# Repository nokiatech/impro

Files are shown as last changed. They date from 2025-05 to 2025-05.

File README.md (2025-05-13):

# Method for Integrated Microphone Pressure Frequency Response Measurement Using a Probe Microphone (IMPro)

The IMPro method measures the pressure sensitivity frequency response of an integrated microphone device. The measurement can be conducted in a normal office environment as well as under anechoic conditions. 

IMPro publication is available at AES E-Library: https://aes2.org/publications/elibrary-page/?id=22907 

## Equipment:

The equipment recommended for the IMPro measurement consists of signal acquisition hardware, a reference microphone, a probe microphone, a loudspeaker, and mechanical hardware to reliably position the probe microphone's tip at the required position.
Item | Part 
----------|-------------
Probe microphone | GRAS 40SA
Reference microphone | B&K 4136
Loudspeaker | Genelec 8010A
Microphone PSU | B&K 2829
Acquisition hardware | RME UFX
Microphone stands | K&M 201A/2
Stereo T-bar | K&M 23550
Tripod universal ball-joint | K&M 19695
Dial gauge positioning arm | Noga MG60103
Thread adapter M8 to 3/8-16 UNC | Custom
Probe microphone holder | 3-D printed part

### Probe microphone holder & 3-D printed part:

The IMPro method uses a probe microphone to measure the pressure at the opening of the microphone sound inlet. The placement of the probe microphone is easier with a help of a probe positioning device to displace the probe tip along the probe tube axis. 

3D printable files and assembly instruction for Probe microphone holder can be downloaded from [Probe holder](https://github.com/nokiatech/impro/tree/main/probe_holder).

## News:
[13.05.2025] IMPro probe mic holder for 3D printing for [Gras 40SA probe microphone](https://www.grasacoustics.com/products/special-microphone/probe-microphones/product/190-40sa)

## Citation

If you find this work useful for your research, please consider citing this paper:

```
@article{cozens2025impro, 
author={cozens  john and hämäläinen  matti and pekkarinen  mikko}, 
journal={journal of the audio engineering society}, 
title={impro -- method for integrated microphone pressure frequency response measurement using a probe microphone}, 
year={2025}, 
number={10225}, 
month={may},}
```

### **Copyright (c) 2025, Nokia Technologies Ltd.**
### **All rights reserved.**

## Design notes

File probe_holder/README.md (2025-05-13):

# PROBE MICROPHONE FINE ADJUSTMENT HOLDER

## DESCRIPTION:
The Probe microphone fine adjustement holder is designed specifically for the GRAS 40SA probe microphone. Use with the B&K probe microphone is not recommended, as the translation axis of the holder is orthoganal to probe tube axis.

The holder fits between the probe microphone and a standard positioning dial guage arm that uses a 1/4" dovetail to connect to a measurement guage - equipment that is commonly used by machinists to setup workpieces in machines.

Provided are STEP 3D files of the parts required. The files are designed such that they can be printed using an FDM printer. The small holes required are not cut/featured in the files, but small indents where the holes are to be drilled are included. 

The holder features a dovetail sliding fit between the upper and lower parts. The dimensions of the dovetail feature were adjusted for the authors FDM printer. Other printers may produce either too tight or too loose fits between the parts. The parts should freely slide together, and there should not be only minimal side-to-side motion of the probe tip due to the fit between the upper and lower parts. If the fit is too tight, then file the mating surfaces. If it is too loose, then either add some material to the STEP files, or offset the 3D printer a fraction of a milimeter. Alternatively add a thin layer of superglue to the mating edges to improve the fit. 

### MANUFACTURE:
The PDF file includes the manual machining steps that are required to make the holder. You will need the following tooling:
1. 3.2mm drill.
2. 2.5mm drill and M3x0.5 tap
3. A drill press is recommended, but a hand drill is possible to use.
4. Two different M3 screws (one countersink head type, and a second machine head screw) plus a M3 nut.
5. Assorted metal files

The parts can be printed with PLA or PETG materials. Other plasics may be OK to use. Metal printed parts may also work. The PDF drawing indicate the surface that is best positioned on the printer bed. The STEP files may be modified to include the hole and thread features as required. 

### ASSEMBLY:
1. The thumb nut and M3 nut should be glued together (super glue). Avoid getting glue in the threads
2. The thumb-screw and M3 machine head screw should also be glued together. It might be a good idea to file the end of the screw to make the surface smooth and reduce the risk of damage to the probe microphone body.
3. Make sure that the probe microphone fits into the hole in the lower part. If it does not fit, use a file or sandpaper to enlarge the hole.
4. The M3 counter sunk screw is inserted into the cut threaded hole and tighted lightly. It is important that the screw head is within the dovetail feature, otherwise the holder will not connect to the positioning arm. A file may be required to ensure this. Some superglue might be needed to make sure the screw stays in place. 
5. Insert the Thumb screw assembly into the threaded hole in the lower part. This screw is used to lock the probe microphone in position. 
6. Slide the upper part into the lower part; the dovetail slides to fit freely, but not have too much lateral movement.
7. Place the Thumb nut into the rectangular cut-out in the lower part, with the M3 nut facing the probe microphone hole. you will need to slide the upper part in or out to allow the thumb nut to engage with the M3 countersunk screw. Tighten the thumb nut to close the space between the upper and lower parts. Never over tighten.

### USE:
1. Attach the holder to the positioning arm. Ensure that the dowvetail locking screw of the positioning arm is tight.
2. Feed the probe microphone cable through the hole in the lower part, and slide the probe microphone body into the lower part. The probe tube should point away from the holder, and the tube should be parallel with the sliding axis of the holder.
3. Lightly tighten the thumbscrew. Too tight risks damaging the probe microphone body. 
4. Adjust the thumb nut so that there is about a 2mm gap between the upper and lower parts.
5. With the holder in the positioning arm, place the probe tip so that it touches the sound inlet of the microphone under test and covers the inlet hole. It is best the probe tube is normal to the device surface curvature at the sound inlet point. 
6. Tighten the positioning arm to lock the probe tip in place
7. Using the thumb nut, move the probe tip away from the device surface by 1mm. Use a 1.0mm feeler guage to determine the gap.

### HINTS:
1. Don't unscrew the thumb nut too much as the upper and lower parts can easily slide apart if gravity acts in the wrong direction. The thumb nut may also go missing in this instance. 
2. A positioning arm that also includes fine adjustment can help, especially if the movement of the holder adjustement and the arm's fine adjustment are in orthoganal directions.

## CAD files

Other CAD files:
probe_holder/LowerPart.stp
probe_holder/ThumbNut.stp
probe_holder/UpperPart.stp
probe_holder/ThumbScrew.stp

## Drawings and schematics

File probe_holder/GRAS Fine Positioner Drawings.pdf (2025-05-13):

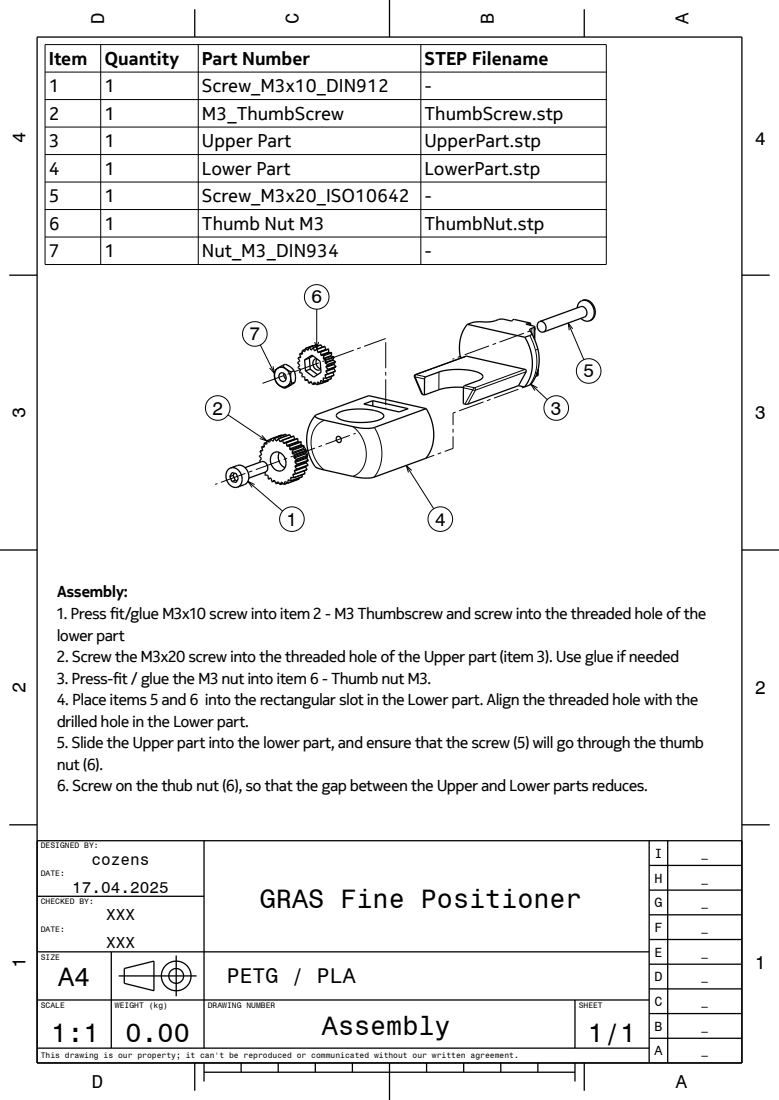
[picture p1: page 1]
XXX DATE: XXX

Item | Quantity | Part Number | STEP Filename
1 | 1 | Screw_M3x10_DIN912 | -
2 | 1 | M3_ThumbScrew | ThumbScrew.stp
3 | 1 | Upper Part | UpperPart.stp
4 | 1 | Lower Part | LowerPart.stp
5 | 1 | Screw_M3x20_ISO10642 | -
6 | 1 | Thumb Nut M3 | ThumbNut.stp
7 | 1 | Nut_M3_DIN934 | -

Assembly:
1. Press t/glue M3x10 screw into item 2 - M3 Thumbscrew and screw into the threaded hole of the
lower part
2. Screw the M3x20 screw into the threaded hole of the Upper part (item 3). Use glue if needed
3. Press-t / glue the M3 nut into item 6 - Thumb nut M3.
4. Place items 5 and 6 into the rectangular slot in the Lower part. Align the threaded hole with the
drilled hole in the Lower part.
5. Slide the Upper part into the lower part, and ensure that the screw (5) will go through the thumb
nut (6).
6. Screw on the thub nut (6), so that the gap between the Upper and Lower parts reduces.

DESIGNED BY: cozens DATE: 17.04.2025 CHECKED BY: | GRAS Fine Positioner | I | _

SIZE A4 | | | | PETG / PLA

SCALE | WEIGHT (kg) | DRAWING NUMBER Assembly | SHEET

This drawing is our property; it can't be reproduced or communicated without our written agreement.

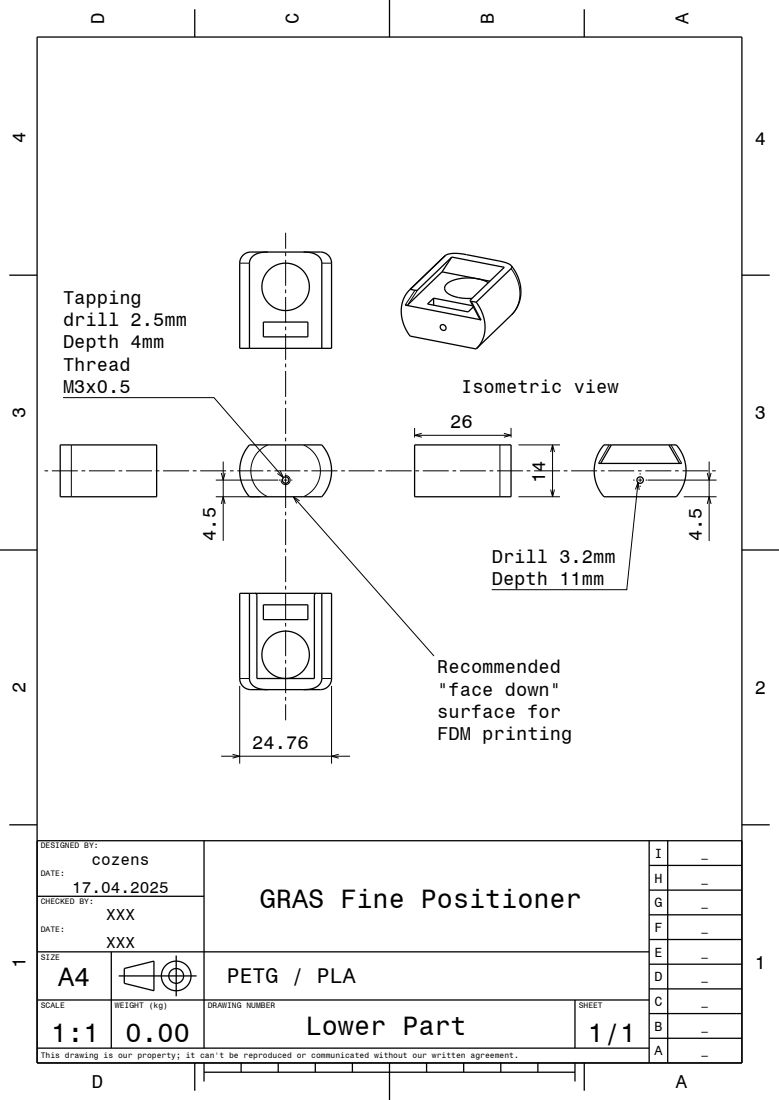
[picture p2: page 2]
Recommended "face down" surface for FDM printing; XXX DATE: XXX; Tapping drill 2.5mm Depth 4mm Thread M3x0.5; Drill 3.2mm Depth 11mm; Isometric view

DESIGNED BY: cozens DATE: 17.04.2025 CHECKED BY: | GRAS Fine Positioner | I | _

SIZE A4 | | | | PETG / PLA

SCALE | WEIGHT (kg) | DRAWING NUMBER Lower Part | SHEET

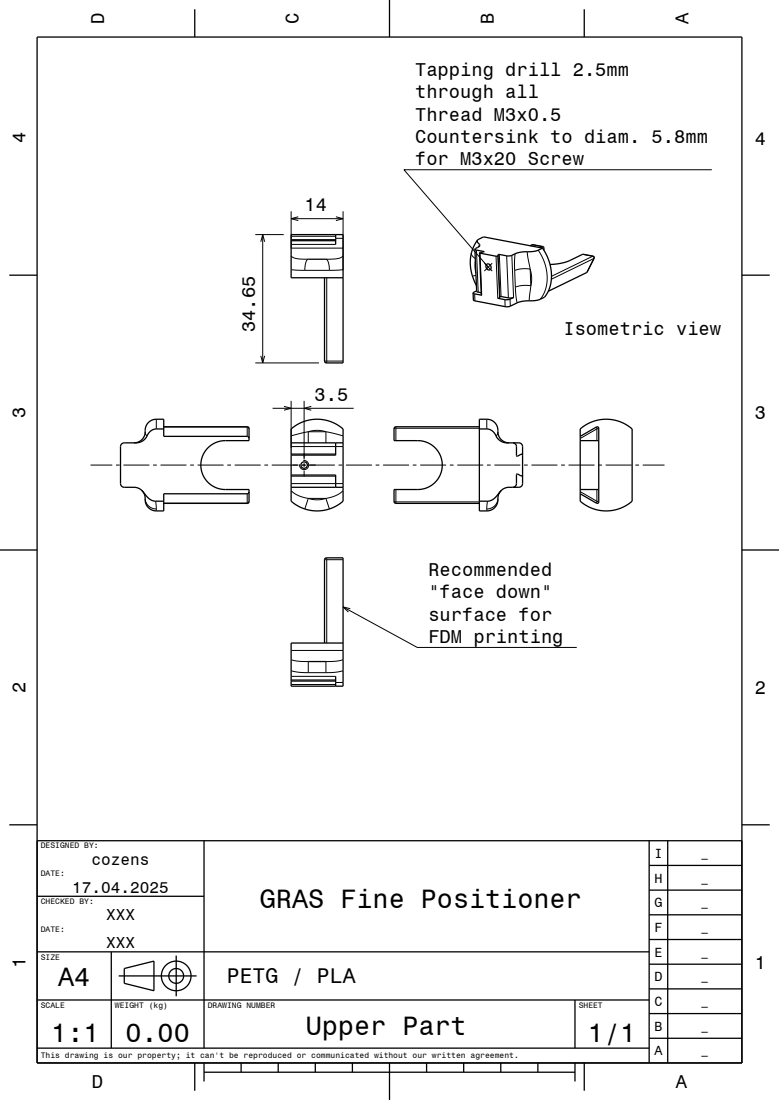
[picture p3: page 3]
XXX DATE: XXX; Recommended "face down" surface for FDM printing; 34.65 Isometric view

Tapping drill 2.5mm
through all
Thread M3x0.5
Countersink to diam. 5.8mm
for M3x20 Screw

DESIGNED BY: cozens DATE: 17.04.2025 CHECKED BY: | GRAS Fine Positioner | I | _

SIZE A4 | | | | PETG / PLA

SCALE | WEIGHT (kg) | DRAWING NUMBER Upper Part | SHEET

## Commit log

2025-05-13 Probe holder STP file upload
    [LowerPart.stp, ThumbNut.stp, ThumbScrew.stp, UpperPart.stp]
2025-05-13 Update STP files for LFS
    [LowerPart.stp, ThumbNut.stp, ThumbScrew.stp, UpperPart.stp]
